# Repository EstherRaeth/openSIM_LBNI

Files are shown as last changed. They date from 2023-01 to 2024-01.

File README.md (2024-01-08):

logo_openSIM_2_web

## open-source structured illumination add-on for fluorescence microscopes

The resolution of conventional optical microscopes is limited by light diffraction to about 200nm. Several superresolution techniques have been recently developed to overcome this limit. Among them, **SIM (structured illumination microscopy)** is one of the most suited for biological imaging.

The **open source hardware project openSIM** is an **add-on** designed at the *Laboratory for Bio- and Nano- Instrumentation (LBNI, EPFL)* (https://www.epfl.ch/labs/lbni/) to **upgrade conventional fluorescence microscopes for superresolution imaging**. The openSIM is an open-source hardware project which has been designed specifically so that it can be built easily by other researchers using the documentation. Our goal is to reach labs worldwide and build a vibrant **open-hardware community**.

complete_system_plus_interfaceBox

**Here you can find a schematic of the general structure of the openSIM documentation**
overview_documentation

A detailed documentation with all the information to build and use the openSIM is provided on our openSIM webpage: 
**https://opensim.notion.site/**

All the files that need to be downloaded in order to assemble and operate the openSIM can be found in this repository. 
More information about the structure of this repository can be found in the README file in the download folder.

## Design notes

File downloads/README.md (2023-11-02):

## Navigating through the openSIM repository:

Below you can find the folder structure and the file content. 
Each folder contains README files with further information about the corresponding file. 

**CAD**
- 3D printing
- laser cutting
- machining
- Solidwork files

**electronics**
- PCB design

**software**
- image acquisition
- image processing

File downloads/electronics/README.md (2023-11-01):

**Electronics folder structure**

electronics_folderStructure

**Electronics folder content**

The files in the folder 'CAMOutputs' are required when ordering the PCB. 

(GerberFiles: Gerber files are a standard file format used in the manufacturing of printed circuit boards (PCBs). These files contain the information necessary to guide the PCB fabrication process and ensure that the PCB is manufactured to the design specifications. Gerber files typically include data on the various layers of the PCB, such as the copper traces, solder mask, silkscreen, drill holes, and other relevant features. PCB design software generates these files, and they are then provided to a PCB manufacturer for the production of the actual circuit board.)

In the folder 'additional information' information on the PCB population can be found. The folder contains also a subfolder 'EAGLE_files' containing the PCB design files (.brd, .sch) in case a user seeks more information or wants to modify the board. These files have to be opened with the Eagle (electronic design software). A free version of Eagle can be downloaded here: http://eagle.autodesk.com/eagle/software-versions/7

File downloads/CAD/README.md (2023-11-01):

**3D printing:**
Here you can find the parts that need to be 3D printed for the openSIM add-on and interface box in STL format.
This file format is commonly used for 3D printing and is compatible with standard commercial 3D printers. 

**laser_cutting:**
Here you can find the parts that need to be laser cut for the openSIM add-on enclosure in DXF format 

**machining:**
Here you can find a drawing indicating the position of the holes that need to be drilled into the heat sink (LED cooling). 

**solidwork files:**
Here you find all parts and assemblies (SLDASM format) of the openSIM add-on and interface box. 
These files are not necessary for the assembly or usage of openSIM, but can be used for further modifications.

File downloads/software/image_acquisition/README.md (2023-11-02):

We currently offer three software versions to cater to various user requirements (see openSIM website section 'Additional information'-'openSIM software' for more information): 

**Full openSIM LabView Project Versions:** For users seeking to modify or customize the software, we provide two full LabView projects. The first version, "openSIM_software_withCameraControl," integrates complete camera control, including image acquisition and data handling, specifically designed for Andor Zyla and Andor iXon camera models, using the Andor SDK (software development kit) for LabView. 
We don't provide this software version on GitHub as it contains proprietary VIs from the Andor SDK3. However, if the user already has the Andor SDK3 then we can provide this software version on request. The second version maintains the same structure but omits camera-model-specific components, making it modular and adaptable for other camera models. 
To address the reviewer’s comment, we developed an additional software version based on which we built an application that we now provide on the openSIM repository. 

**openSIM Application (exe):** To overcome the need for any chargeable licenses and to offer a more open-source software option, we created an openSIM software version which allowed us to build an application from it. This software version is designed for user who primarily want to use the software without any need for modification. Running the software version doesn't require any paid software licenses and is not tied to a specific camera model.

overview_software_versions

If you encounter problems with the installation or running the software please check the troubleshooting guide (chapter 8) in the respective user manual.

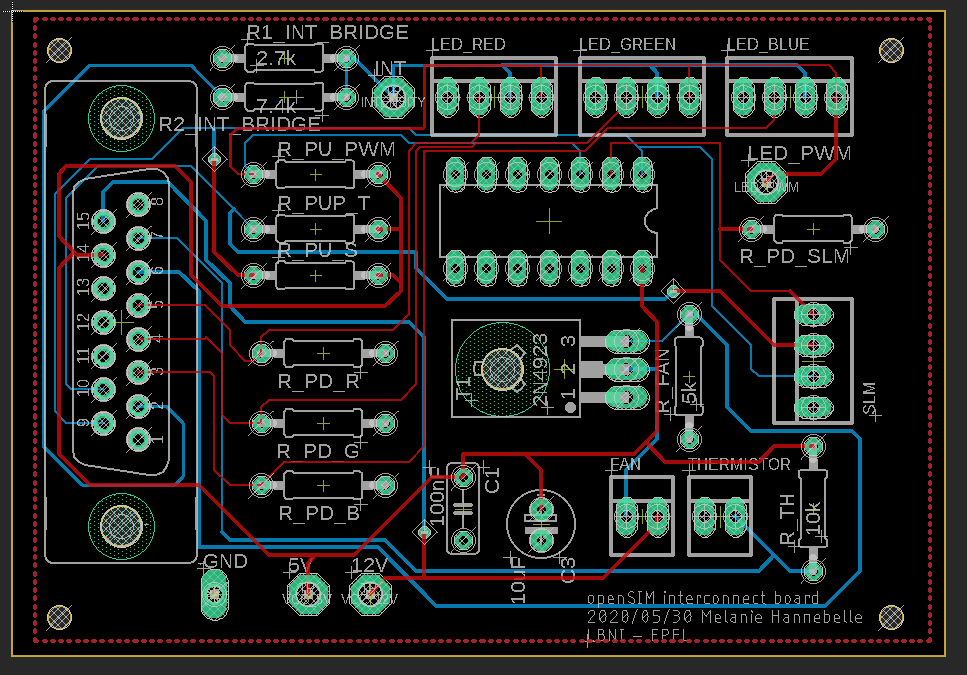
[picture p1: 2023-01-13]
downloads/electronics/additional_information/openSIM_interconnectBoard_PCB_layout.PNG

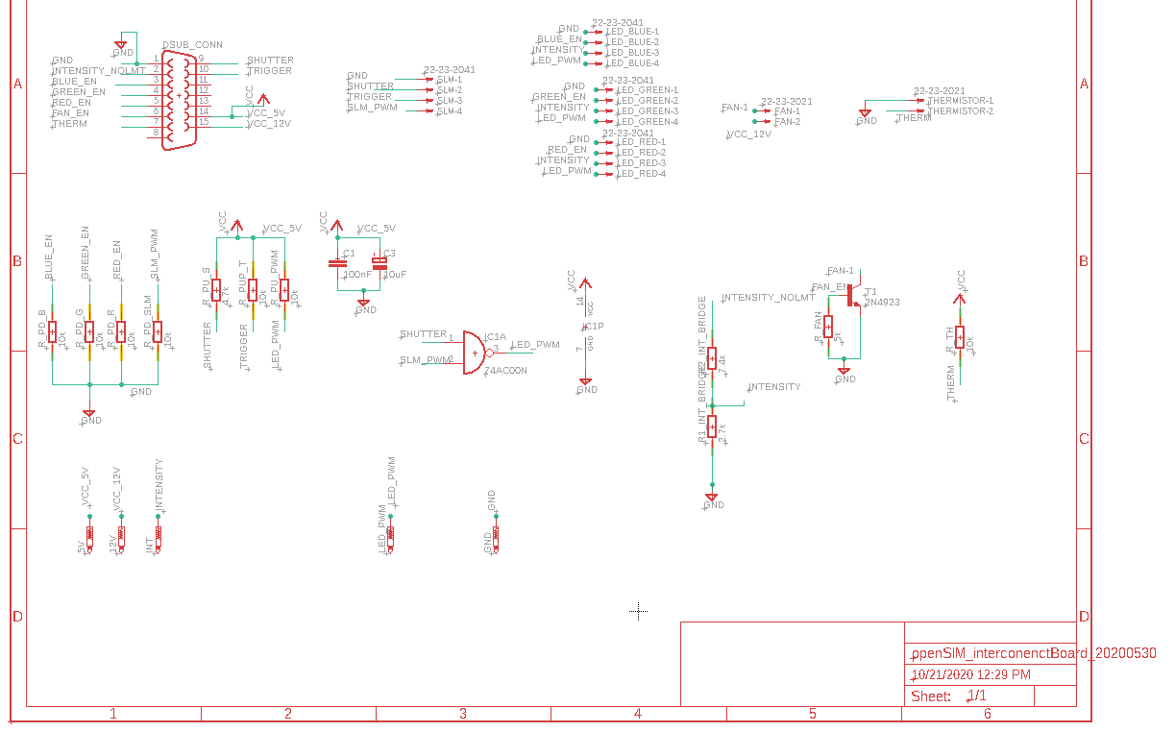
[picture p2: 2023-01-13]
downloads/electronics/additional_information/openSIM_interconnectBoard_PCB_schematic.PNG

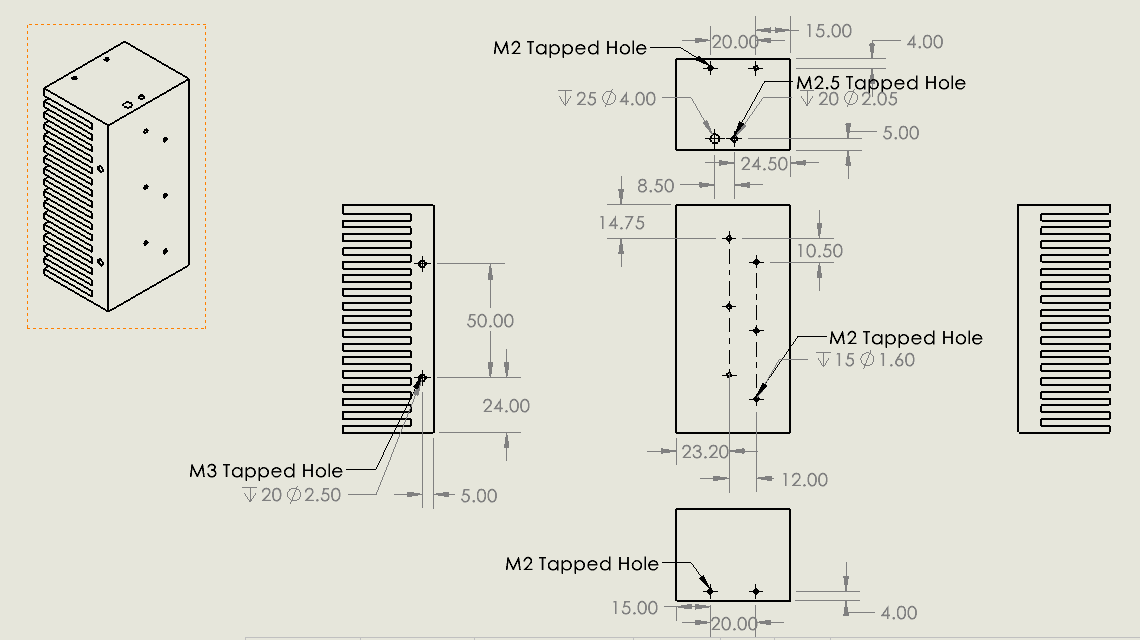
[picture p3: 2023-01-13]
downloads/CAD/machining/drawing_heatSink.png

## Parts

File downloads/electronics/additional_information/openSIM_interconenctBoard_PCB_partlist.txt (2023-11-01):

Partlist

Exported from openSIM_interconenctBoard_20200530.brd at 5/30/2020 7:35 PM

EAGLE Version 9.5.2 Copyright (c) 1988-2019 Autodesk, Inc.

Assembly variant: 

Part       Value          Package      Library       Position (mil)        Orientation

5V         PTR1PAD1-20    P1-20        testpad       (225 0)               R0
12V        PTR1PAD1-20    P1-20        testpad       (425 0)               R0
C1         100nF          C050-025X075 rcl           (725 275)             R270
C3         10uF           E2,5-6E      rcl           (975 225)             R270
DSUB_CONN                 F15V         con-subd      (-375 875)            R270
FAN        22-23-2021     22-23-2021   con-molex     (1300 250)            R0
GND        PTR1PAD1-13Y   P1-13Y       testpad       (25 0)                R0
IC1        74AC00N        DIL14        74xx-eu       (1000 1200)           R180
INT        PTR1PAD1-20    P1-20        testpad       (475 1600)            R0
LED_BLUE   22-23-2041     22-23-2041   con-molex     (1775 1600)           R0
LED_GREEN  22-23-2041     22-23-2041   con-molex     (1300 1600)           R0
LED_PWM    PTR1PAD1-20    P1-20        testpad       (1700 1325)           R0
LED_RED    22-23-2041     22-23-2041   con-molex     (825 1600)            R0
R_FAN      5k             0207/10      eagle-ltspice (1450 700)            R90
R_PD_B     50k            0207/10      eagle-ltspice (275 350)             R180
R_PD_G     50k            0207/10      eagle-ltspice (275 550)             R180
R_PD_R     50k            0207/10      eagle-ltspice (275 775)             R180
R_PD_SLM   5k             0207/10      eagle-ltspice (1850 1175)           R180
R_PUP_T    10k            0207/10      eagle-ltspice (250 1175)            R0
R_PU_PWM   10k            0207/10      eagle-ltspice (250 1350)            R0
R_PU_S     10k            0207/10      eagle-ltspice (250 1025)            R0
R_TH       5k             0207/10      eagle-ltspice (1850 275)            R90
SLM        22-23-2041     22-23-2041   con-molex     (1850 750)            R90
T1         2N4923         TO126        transistor    (1050 725)            R90
THERMISTOR 22-23-2021     22-23-2021   con-molex     (1550 250)            R0

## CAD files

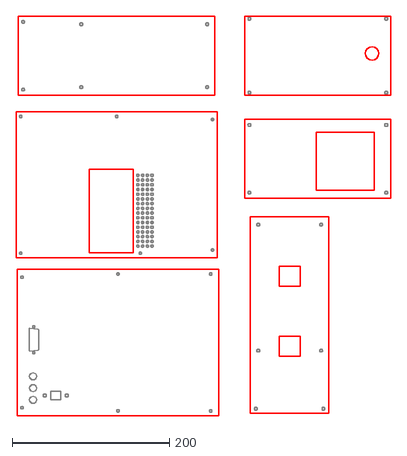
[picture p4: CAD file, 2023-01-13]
downloads/CAD/laser_cutting/assembly_PMMA_lasercut.dxf
476.8 x 507.7

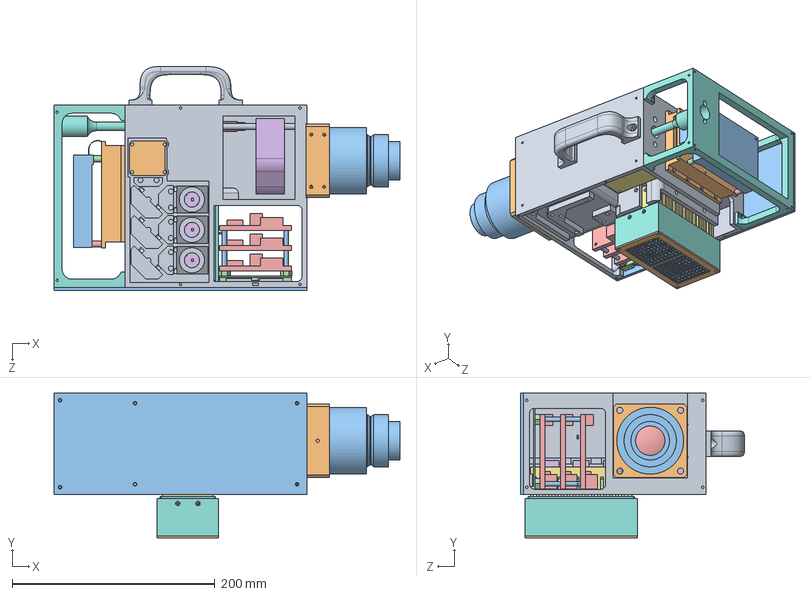
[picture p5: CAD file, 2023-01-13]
downloads/CAD/solidwork_files/openSIM_addOn_assembly/assembly_addOn_openSIM_V2.0.SLDASM
341.7 x 143.0 x 221.0 mm
optics_bloc_openSIM_V2.0
LCP11_M-thorlabs_openSIM_V2.0
SM2Y1-IllPortConnector_thorlabs_openSIM_V2.0
polarizing_beam_splitter_openSIM_V2.0
TTL200-A-tubelens_thorlabs_openSIM_V2.0
TubeLens_Holder_openSIM_V2.0
SSTMH8B_openSIM_V2.0
LMU_N6_openSIM_V2.0 x 2
ssfj6-100_openSIM_V2.0 x 2
SLM_holder_openSIM_V2.0
SLM_Model_Folded_openSIM_V2.0
SP-J3-8_20200728_openSIM_V2.0 x 2
SP-J3-10_20200728_openSIM_V2.0 x 2
PT54_20200728_openSIM_V2.0 x 3
heat_sink_openSIM_V2.0
fan_holder_openSIM_V2.0
fan_openSIM_V2.0
fan_protection_openSIM_V2.0
LED_boards__holder_openSIM_V2.0
LED_driver_board_openSIM_V2.0 x 3
LED_board_spacer_openSIM_V2.0 x 8
LBNR2_openSIM_V2.0 x 4
board_interface_openSIM_V2.0
structure_frame_openSIM_V2.0
handle_openSIM_V2.0
PBS_cover_openSIM_V2.0
panel_bottom_openSIM_V2.0
HANS10_60_3_openSIM_V2.0
HANS10_60_5_openSIM_V2.0

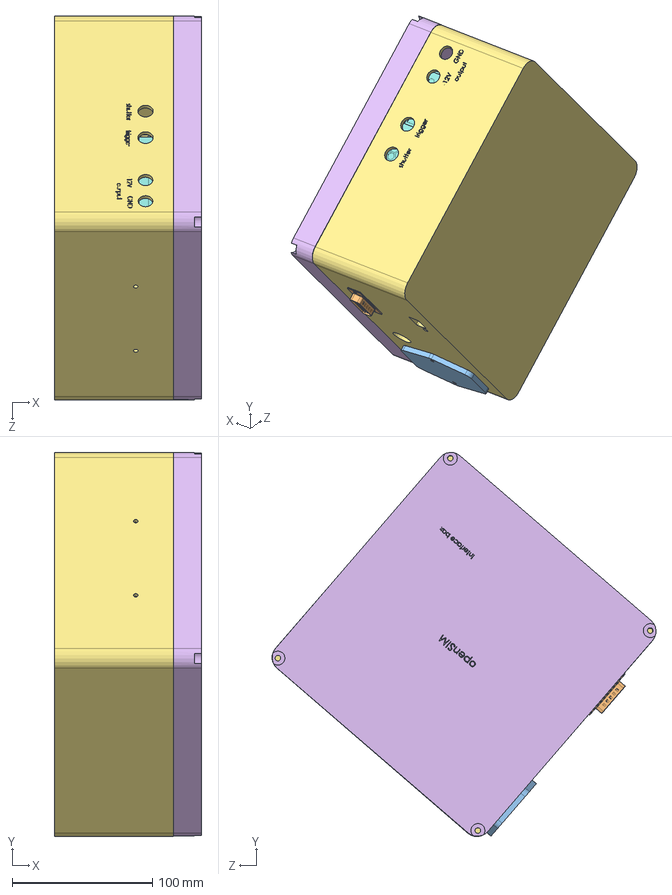
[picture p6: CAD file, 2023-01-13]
downloads/CAD/solidwork_files/openSIM_interfaceBox_assembly/Assem_openSIM_interfaceBox_2powerSupplies_openSIM_V2.0.SLDASM
105.0 x 274.0 x 274.0 mm
clamp_DAQ_openSIM_V2.0 x 2
D SUB 15P male_openSIM_V2.0
delta_06ab2d_openSIM_V2.0
interfaceBox_holder_powerSupply_openSIM_V2.0
NI_USB_6001_daq_openSIM_V2.0
openSIM_interface_box_cover_openSIM_V2.0
openSIM_interface_box_lowerPart
powerSupply1_openSIM_V2.0
powerSupply2_openSIM_V2.0

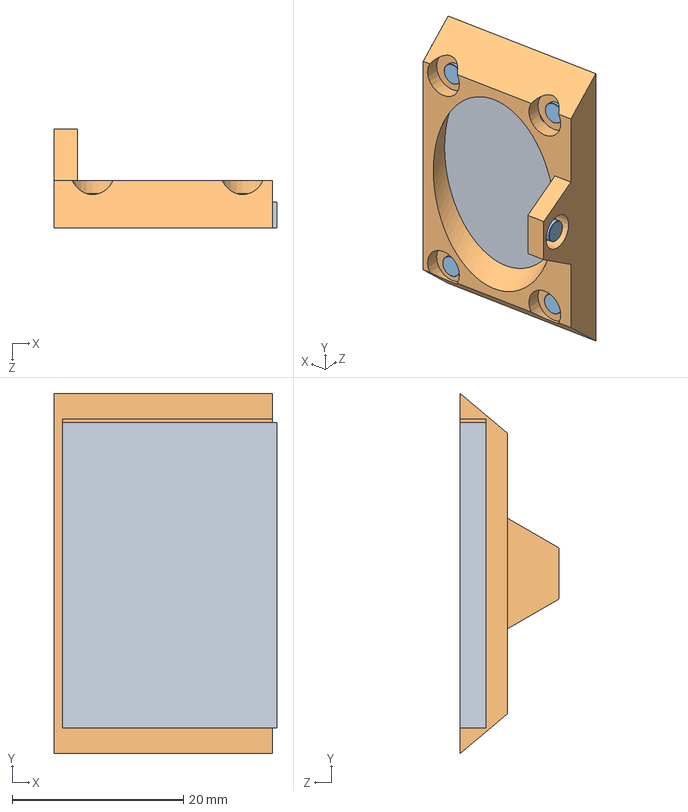
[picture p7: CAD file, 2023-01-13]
downloads/CAD/solidwork_files/openSIM_addOn_assembly/assembly_holder_mirror_20200806.SLDASM
26.0 x 42.0 x 11.5 mm
mirror_20200728
holder_mirror_20200806
HXN3_1_20200728 x 5

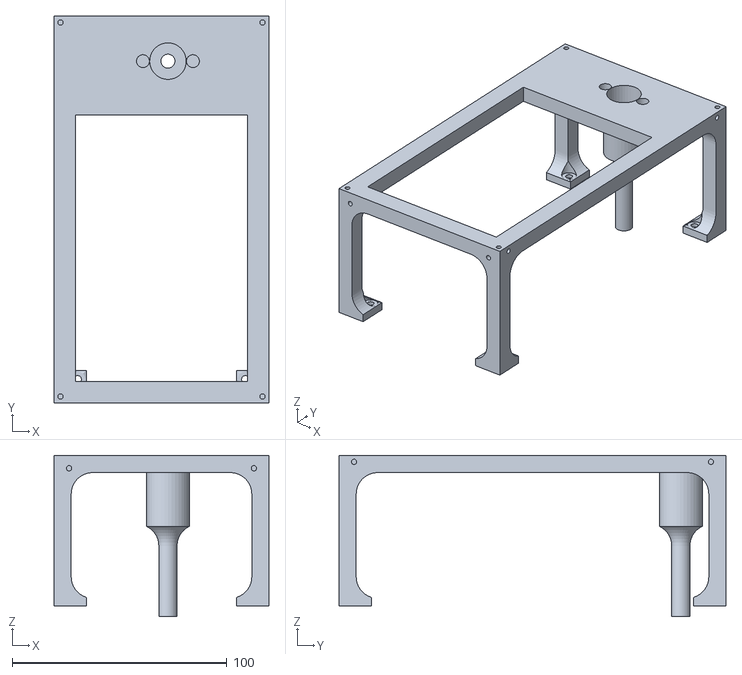
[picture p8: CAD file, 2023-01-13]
downloads/CAD/3D_printing/add_on/structure_frame_openSIM_V2.0.STL
100.0 x 180.0 x 75.0

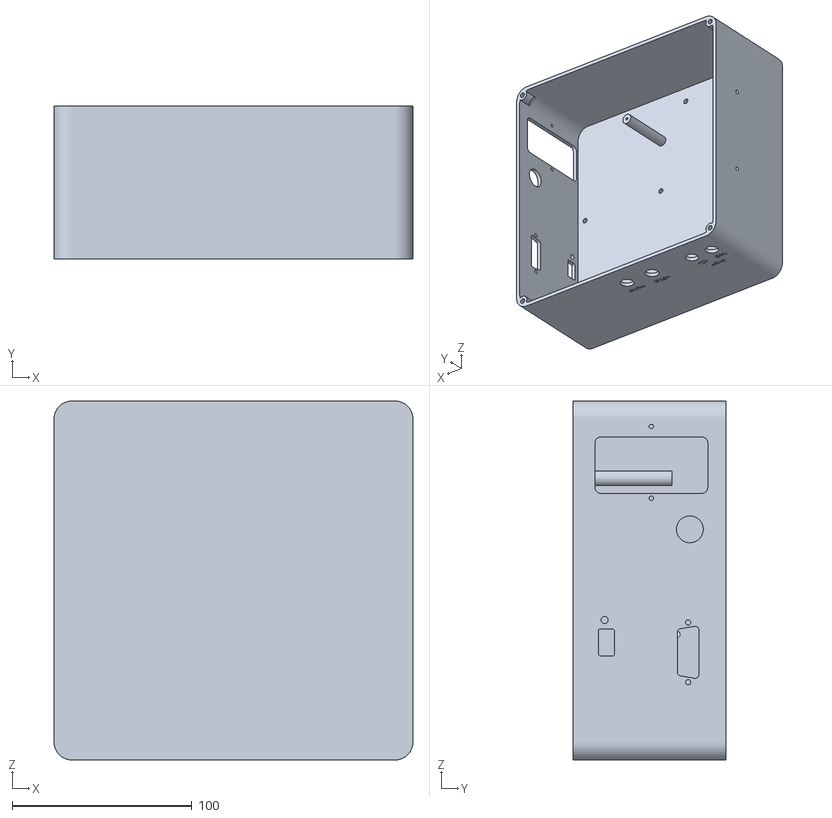
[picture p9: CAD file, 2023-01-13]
downloads/CAD/3D_printing/interface_box/openSIM_interface_box_lowerPart.STL
200.0 x 85.0 x 200.0

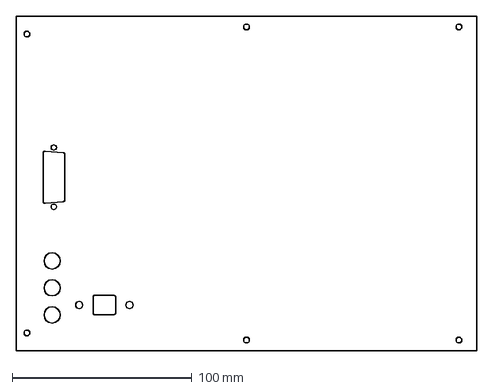
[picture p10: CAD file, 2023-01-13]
downloads/CAD/laser_cutting/panel_front_openSIM_V2.0.DXF
256.0 x 186.0 mm

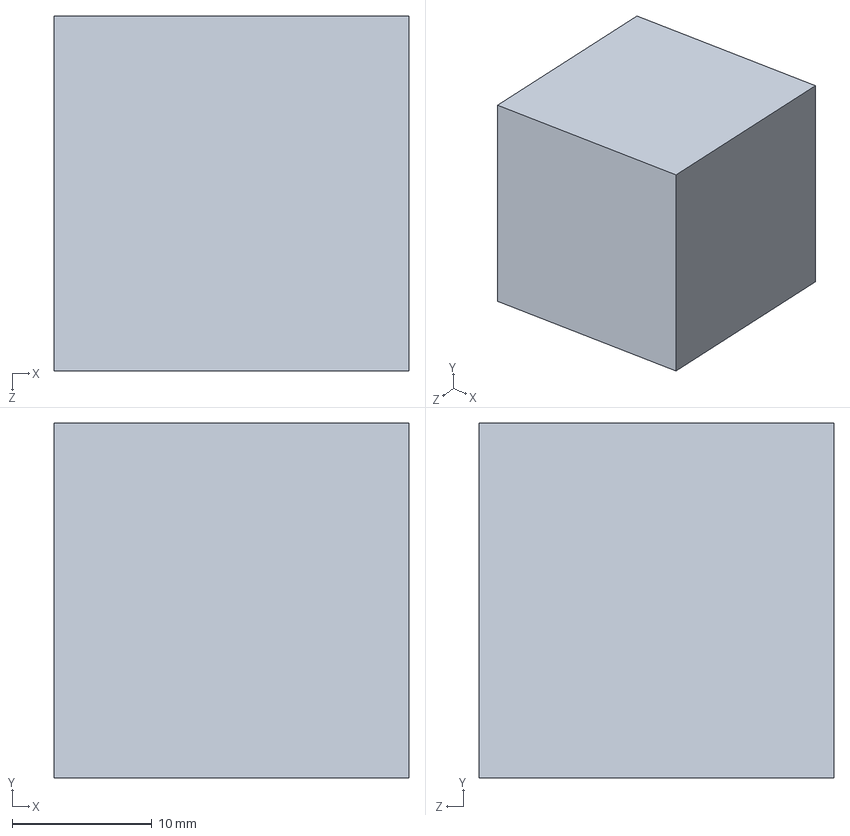
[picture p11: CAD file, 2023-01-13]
downloads/CAD/solidwork_files/openSIM_addOn_assembly/polarizing_beam_splitter_openSIM_V2.0.SLDPRT
25.4 x 25.4 x 25.4 mm

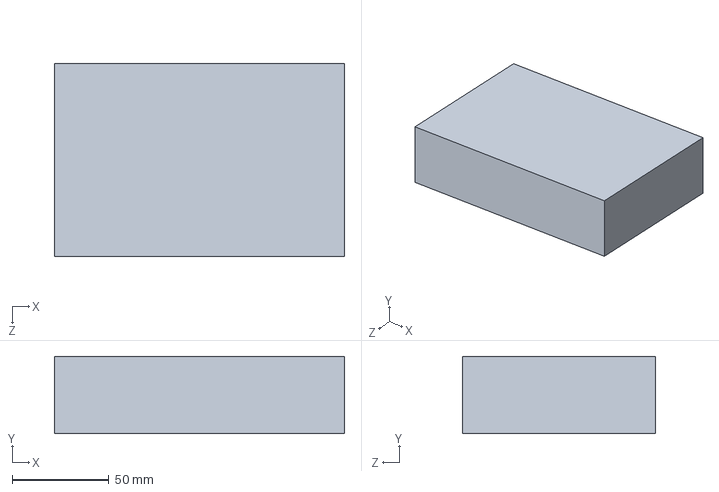
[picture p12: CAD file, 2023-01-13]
downloads/CAD/solidwork_files/openSIM_interfaceBox_assembly/powerSupply2_openSIM_V2.0.SLDPRT
150.0 x 40.0 x 100.0 mm

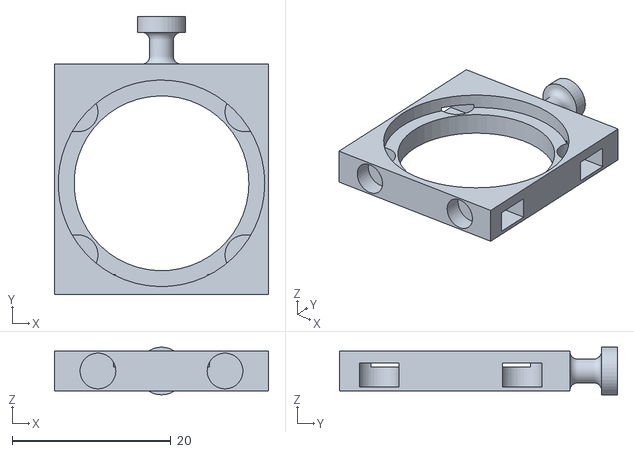
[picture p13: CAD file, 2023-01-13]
downloads/CAD/3D_printing/add_on/collimator_lens_holder_openSIM_V2.0.STL
27.0 x 35.0 x 6.00

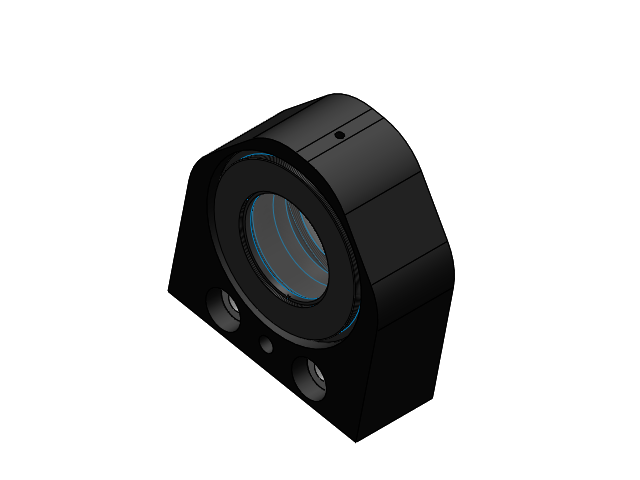
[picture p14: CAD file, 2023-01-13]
downloads/CAD/solidwork_files/openSIM_addOn_assembly/assembly_tube_lens_openSIM_V2.0.SLDASM
TTL200-A-tubelens_thorlabs_openSIM_V2.0
TubeLens_Holder_openSIM_V2.0
SSTMH8B_openSIM_V2.0
LMU_N6_openSIM_V2.0 x 2

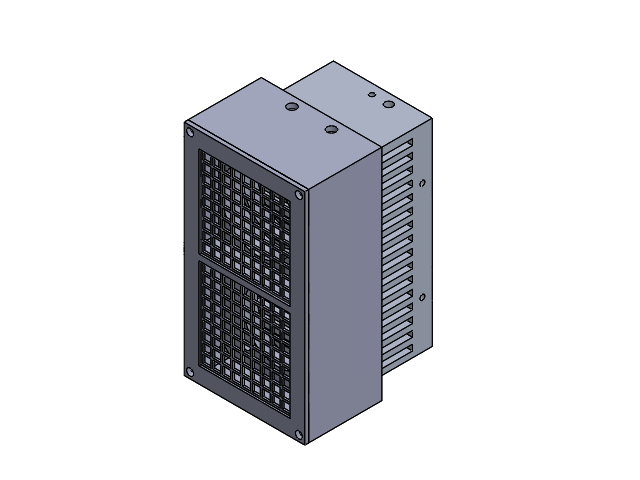
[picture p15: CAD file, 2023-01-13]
downloads/CAD/solidwork_files/openSIM_addOn_assembly/assembly_LEDs_openSIM_V2.0.SLDASM
PT54_20200728_openSIM_V2.0 x 3
heat_sink_openSIM_V2.0
fan_holder_openSIM_V2.0
fan_openSIM_V2.0
fan_protection_openSIM_V2.0

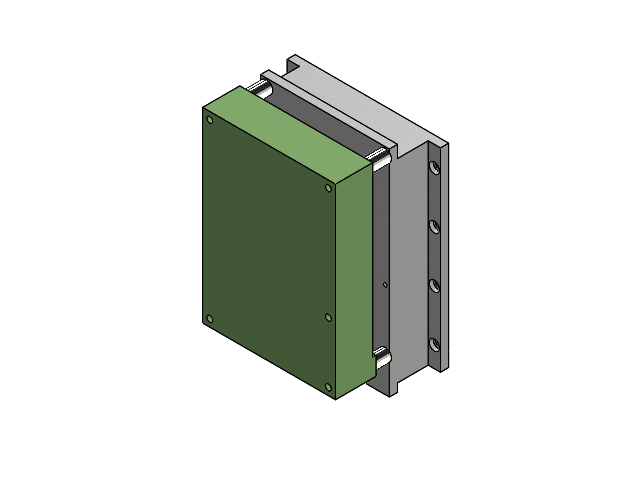
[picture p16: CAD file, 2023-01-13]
downloads/CAD/solidwork_files/openSIM_addOn_assembly/assembly_slm_openSIM_V2.0.SLDASM
SLM_holder_openSIM_V2.0
SLM_Model_Folded_openSIM_V2.0
SP-J3-8_20200728_openSIM_V2.0 x 2
SP-J3-10_20200728_openSIM_V2.0 x 2

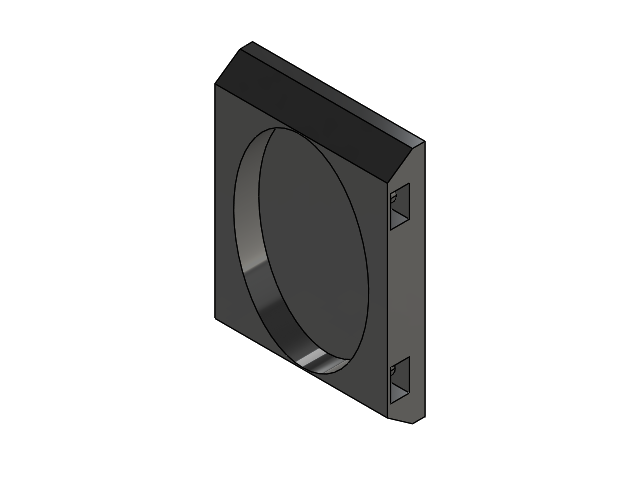
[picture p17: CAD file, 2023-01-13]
downloads/CAD/solidwork_files/openSIM_addOn_assembly/assembly_holder_colorCombiner_dichroic_openSIM_V2.0.SLDASM
HXN3_1_openSIM_V2.0 x 4
holder_colorCombiner_dichroic_openSIM_V2.0
dichroicMirror_openSIM_V2.0

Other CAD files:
downloads/CAD/solidwork_files/openSIM_addOn_assembly/assembly_collimator_openSIM_V2.0.SLDASM
downloads/CAD/solidwork_files/openSIM_addOn_assembly/assembly_LEDs_boards_openSIM_V2.0.SLDASM
downloads/CAD/solidwork_files/openSIM_addOn_assembly/assembly_polarizer_openSIM_V2.0.SLDASM
downloads/CAD/solidwork_files/openSIM_addOn_assembly/assembly_holder_colorCombiner_mirror_openSIM_V2.0.SLDASM
downloads/CAD/3D_printing/add_on/LED_boards__holder_openSIM_V2.0.STL
downloads/CAD/3D_printing/add_on/SLM_holder_openSIM_V2.0.STL
downloads/CAD/3D_printing/add_on/TubeLens_Holder_openSIM_V2.0.STL
downloads/CAD/3D_printing/add_on/cap_screwdriver_openSIM_V2.0.STL
downloads/CAD/3D_printing/add_on/fan_holder_openSIM_V2.0.STL
downloads/CAD/3D_printing/add_on/fan_protection_openSIM_V2.0.STL
downloads/CAD/3D_printing/add_on/handle_openSIM_V2.0.STL
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

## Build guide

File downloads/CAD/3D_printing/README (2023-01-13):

Here you can find the parts which need to be 3D printed in STL format  (file format commonly used for 3D printing)

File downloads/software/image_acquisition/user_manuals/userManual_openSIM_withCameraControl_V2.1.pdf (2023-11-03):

# User manual openSIM software

# software version: with integrated camera control

## Contents

## 1. Structure openSIM user manual:

- The main part of the user interface describes operating the openSIM software in normal operating mode which includes all the controls and indicators necessary for SIM image acquisition.
- For testing and troubleshooting purposes the expert mode can be used (see appendix) during which additional status and log information are displayed.
- The user interface is categorized in controls (user can enter information) and indicators (information are displayed to user)
- Currently the control for two different cameras (Andor Zyla and Andor iXon) is implemented in the software. As camera setting are mostly specific for one camera type, the corresponding descriptions are marked in grey

## 2. Introduction to the openSIM software

The openSIM software is written with LabView. It controls the openSIM device itself and interfaces additional components such as the camera and piezo focus positioner if available. It includes a user interface to enter the necessary parameters and to display currently executed commands and error messages. The part of the software operating the openSIM device controls the LEDs, provides the pattern sequence for the spatial light modulator (SLM), and actuates the fan. The projected pattern sequences can be selected either manually from a list of pattern sequences or automatically based on parameter inputs from the user. The software handles the image mode selection, saving and formatting of the acquired data and the corresponding metadata. In addition, the software controls the camera for the image acquisition. If a device necessary for z-stacking, such as a piezo focus positioner or a motorized focus controller, is available, the software can be used to perform z-stacking. The z-stacking function automatically changes the focus of the objective by providing an analog output to the focus adjusting device.

The software is written in a modular structure to enable a customization and adaption to different peripheral components such as different camera models or focus adjustment. The current version of the software includes an integration for an Andor Zyla sCMOS, an Andor iXon EMCCD camera (information specifically relevant for these two camera types are marked in grey in the following text) and Piezosystem Jena Mipos 100 piezo focus positioner. For controlling the Andor cameras a software development kit provided by Andor (SDK 3 for LabView) is used. The SDK contains a dynamic library from which we used functions to enable and execute the configuration and data acquisition process of the camera.

See the documentation of openSIM software (provided within the distributed openSIM documentation folder) for more detailed information on the LabView code.

## 3. Installation

### 1. Microsoft Visual Studio

Install Microsoft Visual Studio Express 2013. You may encounter compatibility issues if you attempt to run the openSIM software with a different version of Visual Studio. A key is not required for the installation of the Express version.
Download: https://visualstudio.microsoft.com/vs/older-downloads/

This will download an ISO file. To access to setup.exe file in order to install the software you can either mount (right-click on ISO file → mount command) the file (opens a virtual drive that is visible in the file explorer) or extract the files (right-click on ISO file → extract)

### 2. LabView

Install LabView 2018 SP1 including the vision development module and DAQmx module. The openSIM software was created with LabView 2018 SP1.
Download: https://www.ni.com/en-us/support/downloads/software-products/download.labview.html#329059 (https://www.ni.com/en-us/support/downloads/software-products/download.labview.html#329059)
➔ Vision development module: https://www.ni.com/en-us/support/downloads/software-products/download.vision-development-module.html#329460 (https://www.ni.com/en-us/support/downloads/software-products/download.vision-development-module.html)
➔ DAQmx module: https://www.ni.com/en-us/support/downloads/drivers/download.ni-daqmx.html#333268 (https://www.ni.com/en-us/support/downloads/drivers/download.ni-daqmx.html#333268)

### 3. MetroCon

Run the MetroCon 3.3 application from the MetroCon folder provided in the openSIM repository in the image acquisition folder within the software folder
Check that MetroCon is installed in C:\Program Files…

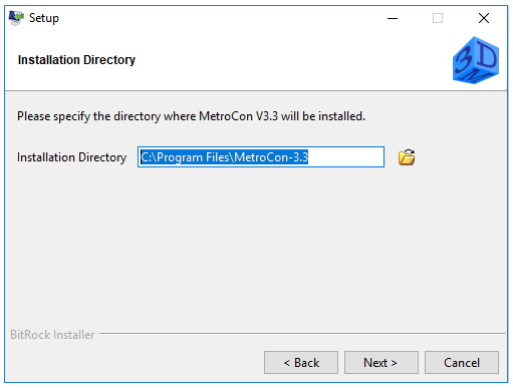
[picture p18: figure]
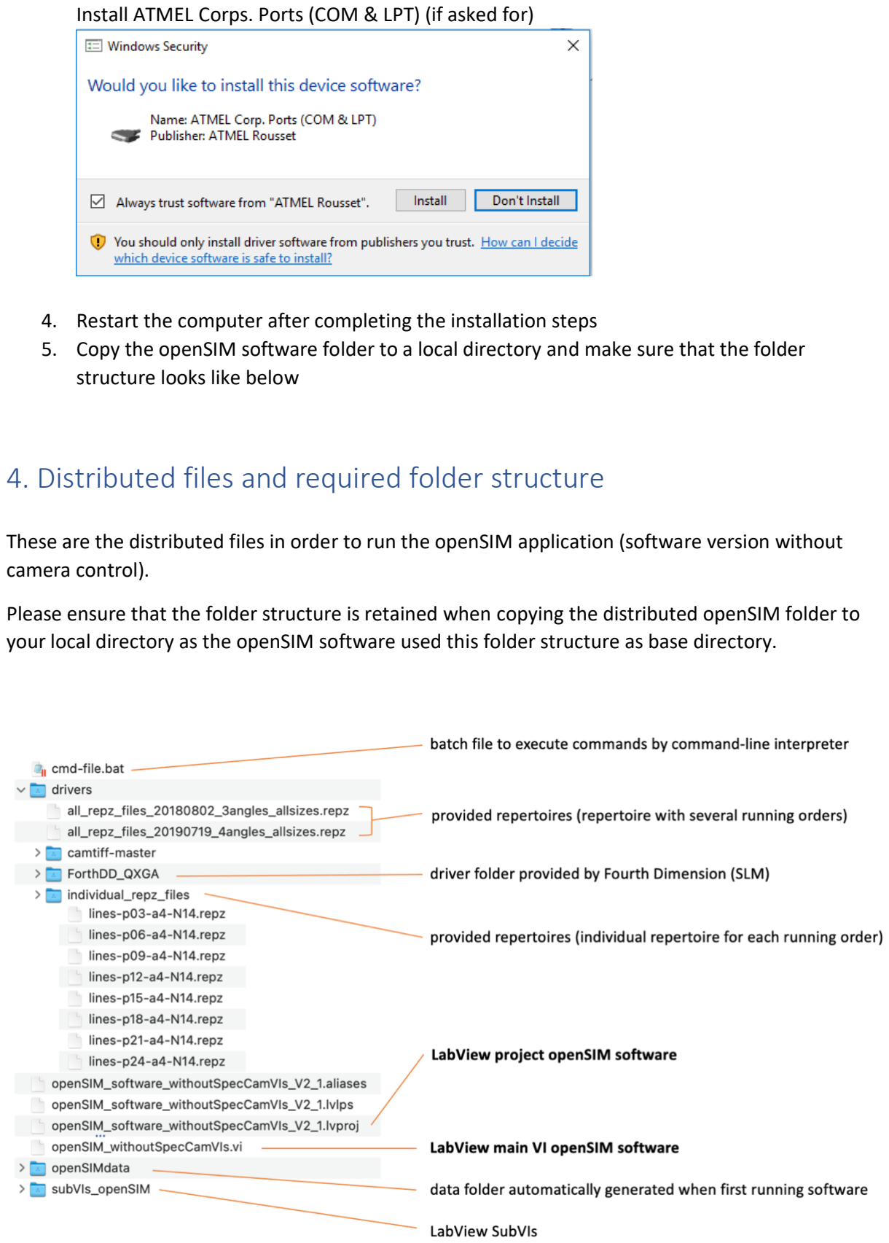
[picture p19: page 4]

Install ATMEL Corps. Ports (COM & LPT) (if asked for)

4. Restart the computer after completing the installation steps
5. Copy the openSIM software folder to a local directory and make sure that the folder structure looks like below

## 4. Distributed files and required folder structure

These are the distributed files in order to run the openSIM application (software version without camera control).

Please ensure that the folder structure is retained when copying the distributed openSIM folder to your local directory as the openSIM software used this folder structure as base directory.

## 5. Illumination patterns

For SIM image reconstruction, the sample needs to be illuminated with a set of patterns with different phases and angles. We generated different line illumination patterns (according to SIMToolbox – supplementary documentation and user’s guide) which are distributed with the openSIM software. For a better understanding we provide here some background information and explain the used terminology.

Pattern sequence:
- sequence of patterns projected by the SLM during the SIM image acquisition
- each pattern of the sequence has a different phase and angle → the number of patterns in the sequence defines the total number of images during one SIM image acquisition (one image is acquired per pattern and the total amount of images is saved as an image stack)
- pattern sequence is stored as repertoire (.repz file format), a zip file containing:
- images of the pattern (.bmp file format)
- timing schedule (.seq file format, supplied by Forth Dimension, defines the bright and dark phases of the SLM)
- running order (.rep file format, describes the order of the projected pattern images in the sequence and the and trigger mode)
- a pattern sequence can contain several running orders (rep file with description of several running orders)
- we provide the generated pattern sequences in two ways:
- repertoire with several running orders (repz files: all_patternSequences_3angles.repz; all_patternSequences_4angles.repz): repertoire to be uploaded to the SLM, the running orders define the different available individual sequences of pattern which can be projected by the SLM
- repertoire with one running order: when using the SIMToolbox for SIM image reconstruction, the software requires information about the pattern sequence projected during the SIM image acquisition, the software can automatically read in the pattern information when stored in a specifically formatted text file (.yaml file format)
→ to facilitate the automatic read in of the pattern description file, we provide a folder (individual_patternSequences) which contains an individual repertoire (repz files: lines-p03-a4-N14.repz, ….) for each running order (lines-p03-a4-N14,…) available in the provided repertoires descripted above (all_patternSequences_3angles.repz; all_patternSequences_4angles.repz), when acquiring a SIM image the individual repertoire corresponding to the used running order is saved together with the acquired data

Terminology for openSIM user interface and user manual:
→ for a better differentiation we use the term ‘repertoire’ for .repz files and the term ‘pattern sequence’ for the actually, by the running order defined and by the SLM projected, sequence of patterns during a single SIM image acquisition

## 6. Control of the openSIM software

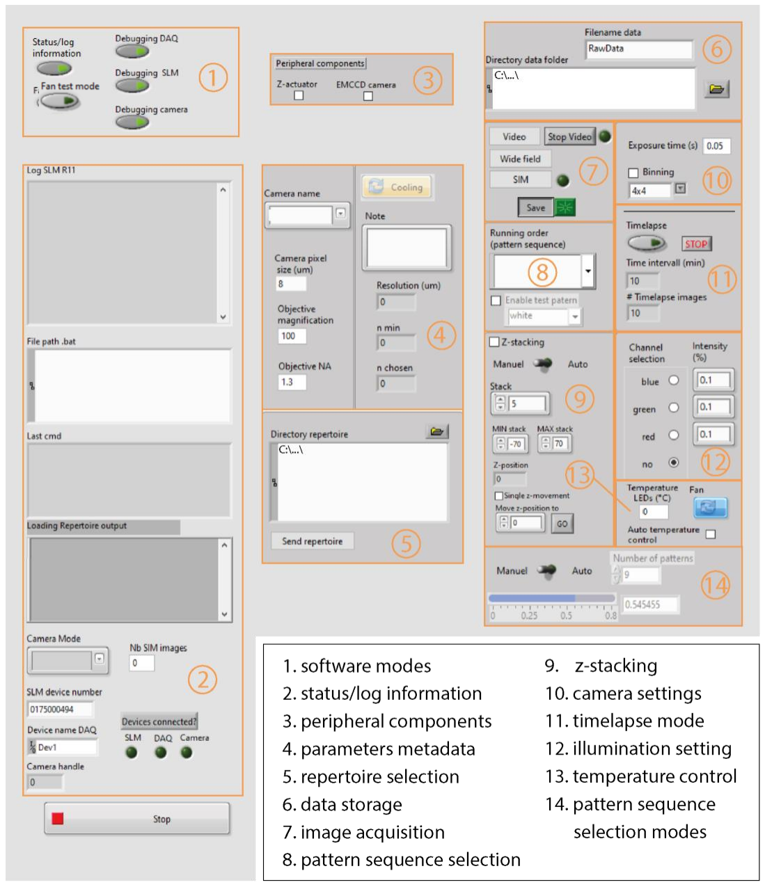
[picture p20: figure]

Overall structure of complete openSIM user interface

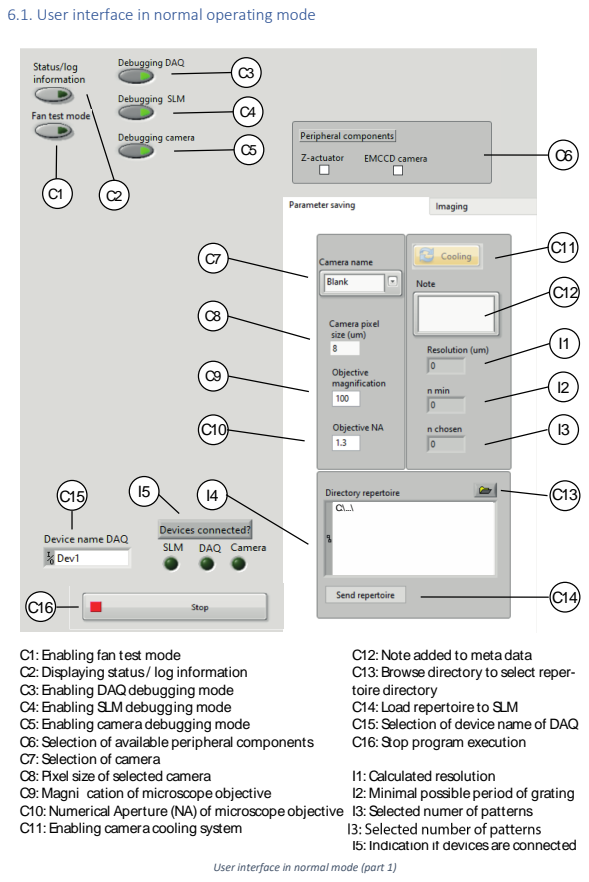
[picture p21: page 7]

6.1. User interface in normal operating mode

C1: Enabling fan test mode
C2: Displaying status / log information
C3: Enabling DAQ debugging mode
C4: Enabling SLM debugging mode
C5: Enabling camera debugging mode
C6: Selection of available peripheral components
C7: Selection of camera
C8: Pixel size of selected camera
C9: Magni cation of microscope objective
C10: Numerical Aperture (NA) of microscope objective
C11: Enabling camera cooling system

C12: Note added to meta data
C13: Browse directory to select reper-
toire directory
C14: Load repertoire to SLM
C15: Selection of device name of DAQ
C16: Stop program execution

I1: Calculated resolution
I2: Minimal possible period of grating
I3: Selected numer of patterns
I4: Directory repertoire
I5: Indication if devices are connected

User interface in normal mode (part 1)

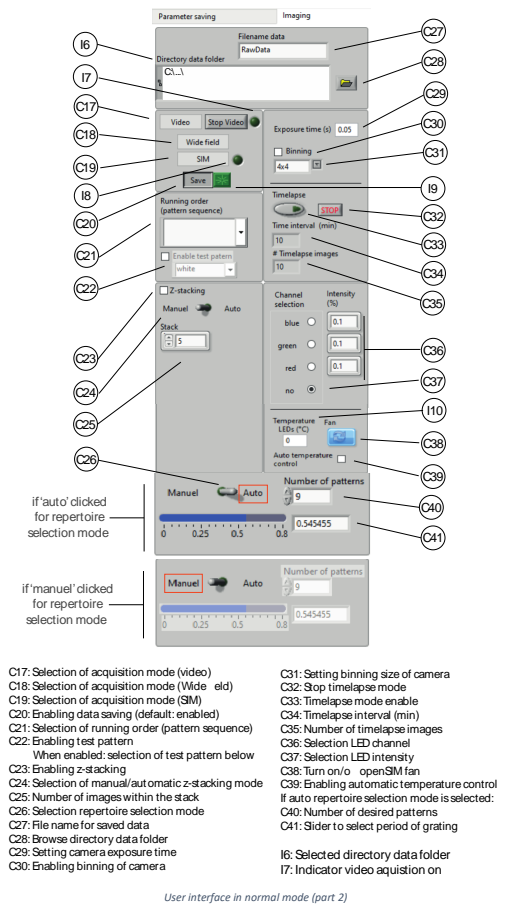
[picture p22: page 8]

C17: Selection of acquisition mode (video)
C18: Selection of acquisition mode (Wide eld)
C19: Selection of acquisition mode (SIM)
C20: Enabling data saving (default: enabled)
C21: Selection of running order (pattern sequence)
C22: Enabling test pattern
When enabled: selection of test pattern below
C23: Enabling z-stacking
C24: Selection of manual/automatic z-stacking mode
C25: Number of images within the stack
C26: Selection repertoire selection mode
C27: File name for saved data
C28: Browse directory data folder
C29: Setting camera exposure time
C30: Enabling binning of camera

C31: Setting binning size of camera
C32: Stop timelapse mode
C33: Timelapse mode enable
C34: Timelapse interval (min)
C35: Number of timelapse images
C36: Selection LED channel
C37: Selection LED intensity
C38: Turn on/o openSIM fan
C39: Enabling automatic temperature control
If auto repertoire selection mode is selected:
C40: Number of desired patterns
C41: Slider to select period of grating

I6: Selected directory data folder
I7: Indicator video aquistion on

User interface in normal mode (part 2)

### 6.2. Input parameters

→ Depending on certain selections/modes some of the indicators and controls are greyed out. These controls and indicators are clickable when the corresponding mode is selected.

INDICATORS:

I1: Calculated resolution in µm
→ based on wavelength of selected channel and NA of objective (C37, C10)

I2: Calculated minimal spatial period
→ only relevant for auto running order (pattern sequence) selection mode
→ based on calculated resolution (I1), camera pixel size (C8) and magnification of objective (C9)

I3: Selected spatial period
→ only relevant for auto running order (pattern sequence) selection mode

I4: Directory of SLM repertoire
→ path to chosen repertoire (.repz file)
→ default: path to the .repz file which is included in the distributed openSIM software folder

I5: Indicator showing if devices (SLM, DAQ, Camera) are connected

I6: Display showing the selected folder where the acquired data is saved in

I7: Indicator showing if video acquisition is currently running

I8: Indicator showing if SIM acquisition is currently running

I9: Indicator showing if saving of the acquired images is currently enabled
→ images are saved in directory selected with C28 and showed in I6

I10: Temperature measured by thermistor at illumination block holding the PT54 LEDs
→ temperature is used as input for the temperature control system
→ if the temperature is too high, the two fans at the aluminum heat sink extender are turned on

CONTROLS:

C1: Enabling/Disabling expert mode (normal mode is default)
→ expert mode includes additional indicators which support debugging (in the expert mode indicator I10-I17 are visible)
→ see appendix for more information about the expert mode

C2: Enabling/Disabling fan test mode
→ if test mode is enabled, only the fan is controlled

Debugging modes:
- In order to facilitate testing and debugging of the software and the individual devices (i.e. SLM, NI DAQ, camera) it can be useful to connect only some of the devices (e.g. only NI DAQ is connected and tested with the software, while the SLM and camera are not connected). However, in the normal (non-debugging) mode the openSIM software will return an error message and stops when devices are not connected (e.g. because of missing device handles when the device is not connected which are needed in the initialization step). In the debugging mode, the software can be used despite the corresponding device not being connected.
- Debugging mode can be used for only one device or several devices at the same time

C3: DAQ debugging mode
→ facilitates the testing of functions independent of the DAQ devise
→ if enabled, the software does not try to connect to the DAQ device, software can be used even if the NI DAQ is not connected

C4: SLM debugging mode
→ facilitates the testing of functions independent of the SLM devise
→ if enabled, the software does not try to connect to the SLM device, software can be used even if the SLM is not connected

C5: Camera debugging mode
→ facilitates the testing of functions independent of camera
→ if enabled, the software does not try to connect to the camera, software can be used even if the camera is not connected

C6: Selecting the available peripheral components
→ specific controls are visible/invisible depending on the availability of the corresponding peripheral component
→ Z-actuator: should be selected if an actuator for changing the z-position of the microscope such as a piezo focus positioner, stepper motor or automated microscope is available and implemented. If enabled, the controls C38-42 are visible
(see section 5 for more information how to implement a z-actuator and see appendix for more information about the user interface for automated z-positioning)
→ EMCCD camera: should be selected if a EMCCD camera, where the EM gain can be changed, is implemented and used. If enabled, the controls C43-C44 are visible
(see section 5 for more information how to implement a camera and see appendix for more information about the additional control for a EMCCD camera)

C7: Selection of camera from list of implemented camera interfaces
→ see appendix for information how to include an interface for a different camera
→ select Andor iXon for Andor iXon EMCCD camera
→ select Andor Zyla for Andor Zyla sCMOS camera

C8: Pixel size of selected camera in µm
→ see the specification sheet of your camera for information about the pixel size → sCMOS camera Andor Zyla 4.2: pixel size is 6.5µm
→ EMCCD camera Andor iXon: pixel size is 13µm

C9: Magnification of microscope objective

C10: Numerical aperture (NA) of microscope objective

C11: Enabling/Disabling cooler (relevant if the camera includes a cooling system)
→ see the specification sheet of your camera to see whether it includes a cooling system
→ see appendix for information about the control of a camera cooling system when including a different camera
→ EMCCD camera Andor iXon has a deep vacuum cooling
→ sCMOS camera Andor Zyla 4.2 has no cooling option

C12: saved note in SIM mode
→ when acquiring SIM images, a text file containing meta data such as the imaging parameter settings are saved
→ the inserted note is added to the saved text file in SIM mode

C13: Browse directory to select file path to the repertoires (.repz file)
→ selected repertoire which is loaded to the SLM
→ default: path to the file ‘all_patternSequences_4angles.repz’

C14: Loading repertoires to SLM (selected with C13 and displayed at I4)

→ repertoires (.repz file) have to be loaded only once to the SLM

C15: Device name of connected data acquisition (DAQ) device
→ device name is shown when USB cable of DAQ device is connected to the PC
(see operation instructions for more information)

C16: Stop button to stop the program execution

C17: Selection of acquisition mode → video: mainly for test purpose, continuous acquisition of widefield images without a saving option

C18: Selection of acquisition mode → widefield: acquisition of widefield images, default: one image is acquired when bottom is clicked, if z-stacking is
enabled: number of total images equals number of stacks (C25) C19: Selection of acquisition mode → SIM: acquisition of SIM image stack, number of total images depends on the number of patterns in selected pattern sequence and number of stacks (C25) if z-stacking is enabled

C20: Enabling/Disabling data saving
→ acquired data is saved as .tiff file
→ in the SIM mode, the metadata (number of SIM datasets, number of pixels (x,y), camera pixel size, exposure time, EM gain, microscope magnification, channel selection) is saved as .txt file located at the file path specified by saving path (I6), saving is enabled by default

C21: Selection of running order (pattern sequence) selection mode
→ manual running order selection mode: the user manually selects the running order (pattern sequence from the list of running orders available for uploaded repertoire in the dropdown menu → auto running order selection mode: the control serves as a display which shows the automatically chosen running order (see C21 for more information about the running order selection mode)

C22: Enabling/Disabling test pattern
→ default: test pattern disabled (greyed out when test pattern is disabled)
→ if test pattern is enabled, different projected test patterns can be selected
→ possible test pattern: black, white, vertical bars

C23: Enabling/Disabling z-stacking
→ widefield mode: the z-position of the microscope objective is changed in steps and one image is acquired per step, the number of images in the stack is defined by C25
→ SIM mode: the z-position of the microscope objective is changed in steps and for every step several SIM images are acquired, the number of images in the stack in defined by C25 and C36 (default: z-stacking disabled)

C24: Selecting manual or automatic z-stacking mode
→ manual mode: the user has to select the starting z-position of the microscope objective and has to manually change the z-position by using the focus adjustment knob of the microscope before acquiring the next image of the z-stack
→ automatic mode: the focus is automatically changed by an actuator according to the z-stacking input parameter during the image acquisitions
(see appendix for more information about the automatic stacking mode)

C25: Number of images in the stack

C26: Running order (pattern sequence) selection mode
→ default: manual mode (if manual mode selected C36, C37 are greyed out)
→ manual mode: the user has to select the desired running order (pattern sequence) from the list of running orders (C21) available for the uploaded repertoire (I4)
→ auto mode: the running order (pattern sequence) is automatically selected based on the selected period (I3) and the desired number of projected patterns in the sequence(C36)

C27: File/folder name of saved data
→ The file name is automatically appended with an XXX-digit number for consecutive images → widefield acquisition mode: inserted name defines the name of the image (.tiff file) which is saved at the location defined by C24 and showed in I6
→ SIM acquisition mode: inserted name defines the name of an automatically created folder where the image (.tiff file), the metadata (.txt file) and the projected pattern (.repz file) are saved in

C28: Browse directory to select path to folder where the data is saved in (default: path to folder ‘openSIMdata’ the directory containing the application)

C29: Exposure time of camera in seconds

C30: Enabling/Disabling binning
→ only implemented for Andor Zyla sCMOS camera
→ sCMOS camera Andor Zyla: if binning is disabled the area of interest (AOI) is set back to 1048 pixel, if binning is enabled the pixel binning is set to the binning size defined by C31

C31: Binning size of camera
→ possible options are 2x2, 3x3, 4x4, 8x8

C32: Stop timelapse mode
→ stops timelapse imaging before last timelapse image is acquired
→ normally timelapse mode stops after acquisition of last timelapse image

C32: Enable timelapse mode
→ only for SIM image acquisition mode
→ if enabled, SIM image stacks are acquired in an interval defined by C34
→ first image is acquired when SIM image acquisition mode is selected (C19)
→ number of acquired SIM images is defined by C35
→ each SIM image stack is saved individual and not as a time stack since individual SIM image stacks are required for image reconstruction

C34: Time interval
→ defines the time period in min between two subsequent SIM image acquisitions

C35: # Timelapse images
→ defines the number of total timelapse images are acquired
→ total timelapse session: time interval * (# Timelapse images – 1)

C36: LED excitation intensity in %

C37: Selection of channel
→ indicates color of excitation light (blue, green, red LED)
(default setting is no LED selected)

C38: Manually turning the two fans which are mounted to the SIM device on/off → are also controlled by an automatic temperature control
→ fans are at the aluminum heat sink extender

C39: Enabling automatic temperature control

C40: Number of desired patterns in pattern sequence
→ relevant for auto running order selection mode

C41: Slider in % (maximum 80% possible)
→ determines how close the period of the grating is to the minimal possible value (I2), selected value is displayed on the right (relevant for auto running order selection mode)

### 6.3. Operating instructions

Running the software with default settings
1. Run the Labview VI ‘openSIM’
2. Select the available peripheral components
→ see appendix for information about possible peripheral components and corresponding differences in the user interface and operational instructions
→ do only select Z-actuator and EMCCD camera if you are sure that the appropriate components are connected
3. Select camera from the list of implemented cameras by clicking on the drop-down menu (C7) → select Andor iXon for Andor iXonUltra EMCCD camera
→ select Andor Zyla for Andor Zyla sCMOS camera
→ select Blank for testing purposes if no camera is connected
→ see appendix for information how to include an interface for a different camera

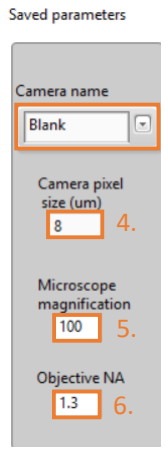
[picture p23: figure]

4. Insert camera pixel size in µm (C8) of selected camera
5. Insert magnification of used microscope objective (C9)
6. Insert NA of used microscope objective (C10)
7. Select ‘Imaging’ tab
8. Insert file name (C27)

3.

7.

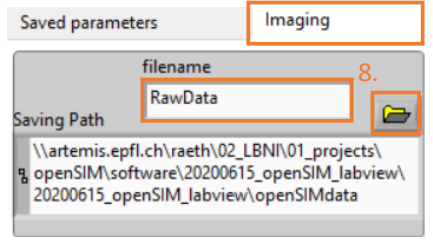
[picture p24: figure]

9.

2.

9. Select saving path (C28) (saving is enabled by default)
10. Select running order (pattern sequence) from list of running orders (C21) by clicking on the drop-down menu

→ naming scheme of running orders:
lines-p45-a4-N14
11. Set exposure time in seconds (C29)

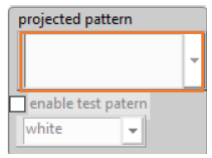
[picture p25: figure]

12. (optional) Enable binning if desired (C31) and select binning

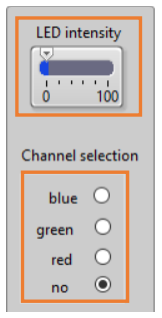
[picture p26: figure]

13. Set LED intensity in % (C36)
14. Select the LED channel (C37) to choose the color of the excitation light
15. Image acquisition (see instructions below)
16. Close the program by clicking stop button on front panel (C16)
→ Important to stop execution by stop button on front panel and not by ‘Abort Execution’ button in the LabView toolbar

Note:

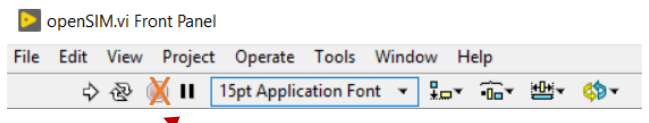
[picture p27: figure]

Repertoires (.repz file) have to be loaded only once to the SLM
→ Selecting repertoire path (C13) and sending repertoire path (C14) should be performed only when using the software for the first time after assembling the openSIM or if the user wants to load additional repertoires to the SLM
grating type | period of grating
number of angles | number of patterns

14.

15.

17.

! Do not stop the program here !

12.

13.

11.

Default settings
- Expert mode: disabled
- Test mode: disabled
- Repertoire path: to the file ‘all_patternSequences_4angles.repz’ in the directory containing the application
- Saving path: to folder ‘openSIMdata’ in the directory containing the application
- Saving: enabled (data is saved with the file ‘RawData’ at the default saving path)
- Fan: turned on
- Running order (pattern sequenc) selection mode: manual
- Test pattern: disabled
- EM gain: disabled

Acquire Data: widefield image
1. Adjust microscope focus to the desired imaging plane
2. Click on the ‘Widefield’ button (C18)

Acquire Data: SIM image
1. Adjust microscope focus (manually or via microscope interface) to the desired imaging plane
2. For timelapse imaging the timelapse imaging mode has to be enabled before next step (Clicking ‘SIM’ button acquires the first timelapse image, the subsequent images are acquired in a sequence defines by C34 and C35)
3. Click on the ‘SIM’ button to acquire a SIM image stack (C19)

Manual z-stacking
→ stacking disabled: one single SIM/widefield image is acquired → stacking enabled: several SIM/widefield images are acquired
1. Enable z-stacking
2. Select manual z-stacking mode
3. Select the number of desired images within the stack
4. Manually select the starting z-position of the microscope objective
5. Click either the Widefield (C18) or the SIM button (C19) depending on the desired imaging mode in order to start the acquisition
6. After every acquired image, a dialog window pops up asking if the next image can be acquired. Before clicking on acquire, change manually the z-position of the objective by using the focus adjustment knob of the microscope. When clicking acquire, the next image will be acquired
7. Repeat step six until all images are acquired

1.

3.

2.

## 7. Data handling

- The acquired data is saved in the selected folder (file name can be seleted with C27, path of folder where data is saved in can be selected with C28 and is shown in I6)
- The data is saved in tiff format (widefield: tiff file with one frame, SIM: tiff file with image stack where the number of frames corresponds to the chosen number of patterns in pattern sequence (shown in I18)
- Along with the tiff image file, the repertoire (repz file with single running order) corresponding to the used running order (pattern sequence) selected with C21 and a file containing the metadata (.txt) (same file name as image file but different file format) is saved
- The metadata file contains information about the used parameters during the image acquisition (e.g., image type, pixel size, number of patterns, LED channel, exposure time)
- The tiff format is a commonly used file format (lossless file format) compatible with ImageJ and the image reconstruction software SIMToolbox (MATLAB toolbox for structured illumination fluorescence microscopy)

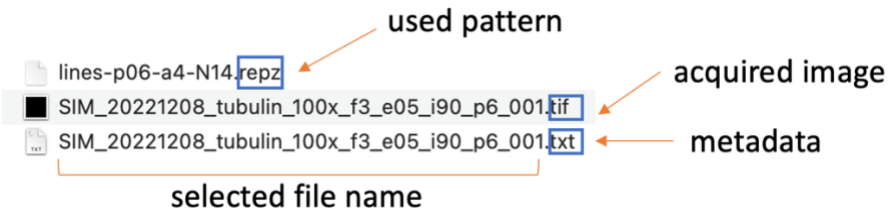
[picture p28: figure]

Example how data is saved during image acquisition

## 8. Troubleshooting

Problem | Possible reason | Possible Solution
When first running the openSIM software, it is not possible to connect to the SLM | The openSIM software might encounter problems connecting to the SLM due to missing drivers | Download the openSIM software file from here (https://zenodo.org/records/10067217) and extract it on your local drive. Try to run the openSIM software from this file.
It is not possible to connect to the NI DAQ, SLM or camera → error message(s), indicator does not light green and software automatically stops execution) → if the openSIM software cannot establish the communication with the SLM and/or DAQ, camera an automatic error message will appear and the | The openSIM software was closed by clicking the ‘Abort execution’ at the Labview toolbar instead of clicking the stop bottom (C16). By clicking the user interface stop bottom it is assured that the NI DAQ, SLM and camera are set back to their default settings and that the devices are closed properly. Not doing so can lead to reconnection problems when subsequently restarting the software. | Close the complete openSIM LabView project and reopen. If this does not solve the problem close the software and dis- and reconnect the individual components. Then start the applications again. If it is still not possible to connect to the devices, close the applications and restart the computer.

software execution is
stopped
Error message: ‘Error 5006 occurred at AT Open A.vi: OUT OF RANGE’ | Camera is physically not connected to the PC | Connect the Andor Zyla camera to the PC via the USB cable
| The openSIM software cannot connect to the camera. This problem can occur if the ‘Abort execution’ at the Labview toolbar is used for stopping the program execution instead of the stop button in the user interface (C16). If the camera is not closed properly, the data structures which are held internally by the SDK are not cleaned up which can lead to problems when reconnecting to the camera. | Disconnect and reconnect the USB cable from the camera to the PC. If this does not solve the problem restart the camera first and if the error message still occurs, then also restart the PC. One can also check if the camera can be accessed via via AndorSolis (Andor’s camera control system)
When enabling z-stacking error message appears | Z-actuator at peripheral component selection is not enabled (C6) | Enable z-actuator and try to enable z-stacking again

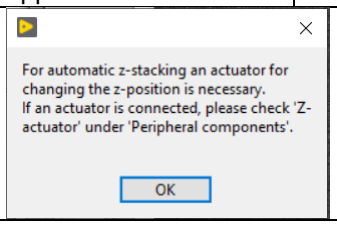
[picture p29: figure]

## 9. Software adaptation

### 9.1. Integration of a different camera

The current version of the software includes an integration for an Andor Zyla sCMOS, an Andor iXon EMCCD camera. In order to integrate another camera to the openSIM software the subVIs listed below have to be adapted. All of these VIs contain a main case structure to differentiate between the implemented cameras. An additional case has to be added to include the necessary code within the subVIs. The camera name has to be added to the Combo Box Camera name to select the corresponding case in the subVIs. Many scientific camera manufacturers provide Labview SDKs for their camera systems which are often structured as libraries containing several subVIs to control the camera. The exact integration of the camera highly depends on the camera type and the camera manufacturer. In the section below the general approach how to implement a different camera into the openSIM software is descripted. For more specific information about the camera-specific SDK please see the information provided by the manufacturer. They are often distributed together with the SDK installation program or accessible online.

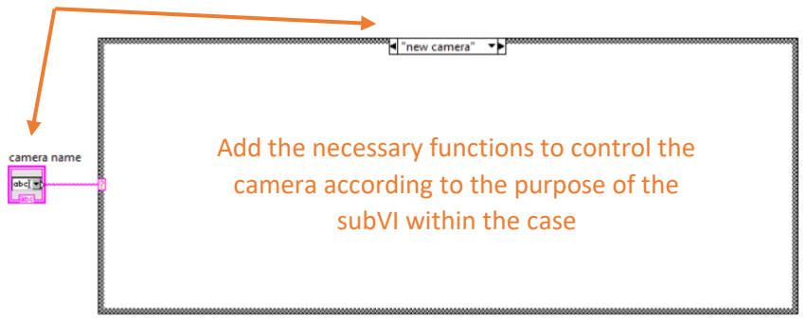
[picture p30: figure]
camera according to the purpose of the subVI within the case

subVi_Initialyse_Camera
- input: Camera name, Em gain enable, Em gain, Exp Time, binning enable, binning size
- output: camera connected?, IMAQ Buffer, Handle, Xpixel, Ypixel

→ in this subVI, the camera/camera specific library has to be initialized and all general and camera specific parameters have to be set in order to run the camera (for more specific information about the camera initialization and the necessary parameters please refer to the information about the corresponding SDK often provided by the camera manufacturer)
→ the indicator camera connected? has to be set true at the end of the subVI if everything was initialized and set correctly
→ EM gain only relevant for EMCCD cameras
→ handle, area of interest (AOI) width, AOI height, Auxiliary (AUX) output source (configures the signal which appears on the AUX output pin of the camera) is relevant when using SDK3 to control sCMOS cameras from Andor

Internal settings for Andor Zyla 4.2 sCMOS camera:
- Pre-amplification gain control: 12-bit (low noise)
- Auxiliary output source: Fire all
- AOI height: 1048px, AOI width: 1048px

Internal settings for Andor iXonUltra EMCCD camera:
- EM gain mode: 8-bit
- Acquisition mode: 1
- Read mode: 4
- Trigger mode: internal
- Acquisition timing: TTL high
- Shutter: auto

EM_gain_enable
- input: EM gain, Handle, Camera name, EM gain enable
→ only relevant when using a EMCCD camera
→ if EM gain is enabled the value for the EM gain has to be set to the value determined by C44

sub_vi_exp_time
- input: Handle, Camera name, Exp time
→ in this subVI the exposure time of camera in seconds has to be set to the value determined

Add a new case to the structure which is selected by the camera name

Add the necessary functions to control the

by C29

subVI_GetImage_Camera
- input: Camera name, IMAQ buffer, Handle, Xpixel, Ypixel
- output: array, array 2D, Display 2
→ in this subVI, the image acquisition has to be implemented including triggering start of image acquisition by the camera, readout data from camera, if necessary, caching in an additional buffer, conversion of byte data into pixel data according to the selected pixel encoding
→ Xpixel / Ypixel are used to create 2D array of pixel data to save the data afterwards (saving has not to be included in the subVI)
→ IMAQ buffer is used to display data

subVI_Close_CamerasubVI_Close_Camera
- input: Camera name, Handle
→ closes camera
→ within the subVI it has to be ensured that the camera is closed properly to ensure a bugless start at the next execution (for many cameras the data structures which are held internally by the SDK have to be not cleaned up)

### 9.2. Integration of a different focus positioning

The implemented z-stacking/single z-movement uses an analog signal via the DAQ device to control a piezo focus positioner (piezo focus positioner Jena Mipos 100 from Piezosystem). The piezo focus lens positioner can move objectives in a precise and accurate way. To do so, the piezo positioner is attached to the standard optical microscope. The objective is then screwed into the piezo positioner instead of the objective turret. In order to use a piezo focus positioner with a different motion range or voltage range but with the same operation principle (see figure 1), the initialization values for the motion and voltage range has to be changed in the initialization frame (first frame in Labview block diagram). If a different actuator type or a different operating principle should be implemented, the subVI subVI_Zstacking_piezo and the cases within the consumer loop have to be changed. Corresponding cases are Z-auto, stacking_off, checking stacking input, single z-movement_on, single z-movement_off.

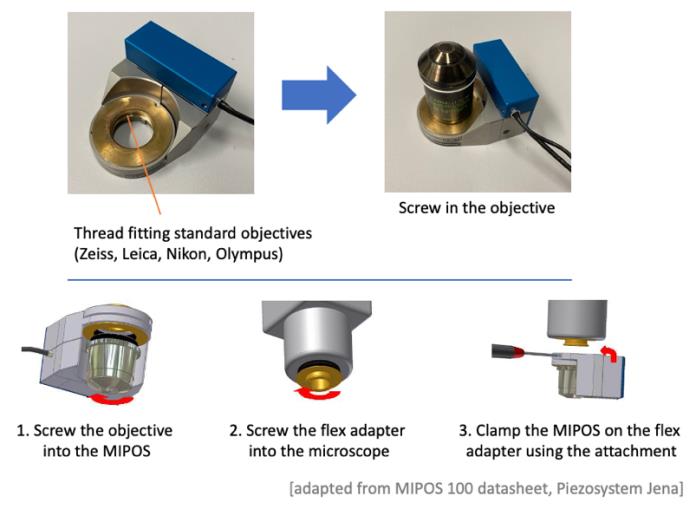
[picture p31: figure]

## Appendix

Installation of Andor SDK3 for LabView
→ LabView has to be installed before installing SDK3 for LabView
1. Run the Andor SDK3 for LabView installer (the SDK can be downloaded at https://andor.oxinst.com/products/software-development-kit/software-development-kit if it is not provided when purchasing the camera)
2. Choose the folder where LabView is installed as folder to install the SDK3 (program files → National Instruments → LabView XXXX) - if several LabView applications are installed (version, application bitness), make sure that the correct one is chosen
→ e.g. C:\Program Files\National Instruments\LabVIEW 20xx
→ e.g. C:\Program Files (x86)\National Instruments\LabVIEW 20xx
→ or corresponding path to the program folder for other operating systems than windows

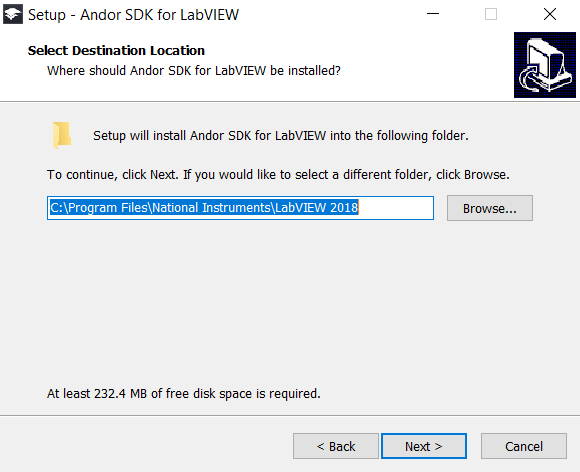
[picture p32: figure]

Status / log information

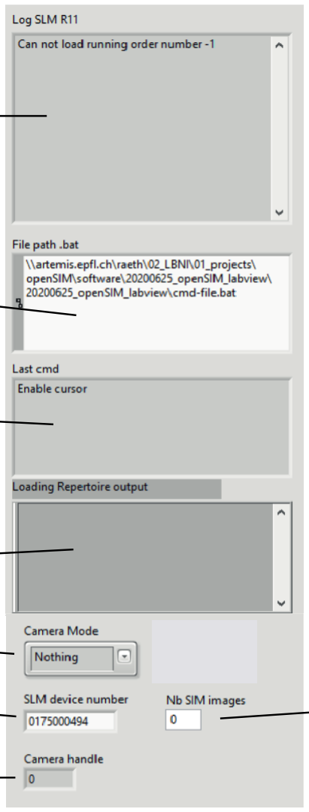
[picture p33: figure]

Figure 1: User interface with status / log information

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
I11: Dislaying current status of SLM
I12: Path to bat le
I13: Last executed command
I14: Text which is passed to command line I15: Current acquistion mode
I16: Device number of SLM
I17: Handle of camera
I18: Number of projected patterns

ADDITIONAL INDICATORS:

I11: Display showing the current status of the SLM R11
→ e.g. bat file cleared/loaded, repertoire loaded, load running order number, cannot load running order number, pattern send, device closed

I12: File path to bat file
→ the bat file contains commands for the SLM in order to load the repertoire
→ see I4 for more information about the repertoire
→ the path should not be changed from the default value.

I13: Display showing the last executed command in the openSIM program

I14: Display showing the text which is passed to the command line in order to run a system command sent to the SLM (bat file to load repertoire)

I15: Current acquisition mode (i.e. video, widefield, SIM)
→ selection via controls C17 (for video), C18 (for widefield), C19 (for SIM)
→ video: mainly for test purpose, continuous acquisition of widefield images,
without a saving option
→ widefield: acquisition mode for widefield imaging, default: one image is acquired when clicking C18, number of acquired images depends on number of stacks (C25)
if z-stacking is enabled
→ SIM: acquisition mode for SIM imaging, number of total images depends on number of patterns in pattern sequence (I17) and number of stacks (C25) if z-stacking is enabled

I16: Device number of connected SLM

I17: Handle to connected camera (relevant for sCMOS camera Andor Zyla)

I18: Number of SIM images/patterns
→ is automatically indicated based on the chosen running order (pattern sequence)

Automatic z-positioning

This section applies only if the piezo focus positioner Jena Mipos 100 (Piezosystem) is used according to the operating principle depicted in figure 5. If a piezo positioner with a different motion and voltage range or a different actuator type is used, please refer to the section 5 for more information about the integration.

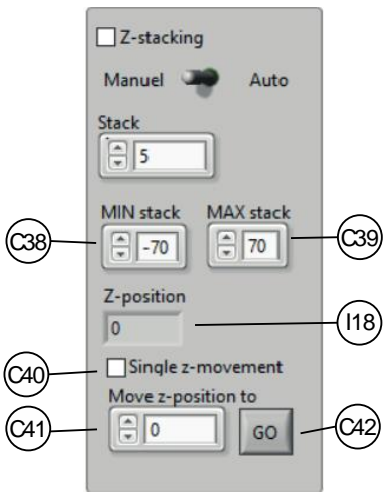
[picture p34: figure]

Figure 2: User interface for automatic z-stacking

ADDITIONAL INDICATOR AND CONTROLS

I16: Current position of z-actuator in µm during z-stacking if z-stacking is enabled

C38/C39: stack range in µm
→ min: z-position of first stack relative to mid-position
→ max: z-position of last stack relative to mid-position
(values have to be within motion range of z-actuator, for MIPOS 100 -70µm – 70µm)

C40: Enabling/disabling single adjustment of z-position by z-actuator
→ if enabled, piezo focus positioner is set to mid-position as initial position (half of its motion range)
C43 | C44

C38: Motion range of z-actuator (min)
C39: Motion range of z-actuator (max)
C40: Enabling single z-movement
C41: Desired z-position within motion range of z-actuator C42: Start single z-movement

I18: current z-position of acutuator during z-stacking

C43: Enable EM gain for EMCCD camera C44: Set EM gain for EMCCD camera

C41 Desired z-position for single z-movement
→ focus positioner moves to inserted z-position in µm relative to mid-position by clicking the GO button (value has to be within motion range of piezo focus positioner, for MIPOS 100 -70µm – 70µm)

C42: Executing single z-movement

OPERATIONAL INSTRUCTIONS FOR AUTOMATIC Z-POSITIONING

Z-stacking:
→ relative to mid-position (half of the piezo motion range), mid-position is used as initial position
1. Enable z-stacking (C23) → piezo is set to mid-position (order important!)
2. Adjust microscope focus (manually or via microscope interface) to the object of interest
3. Set stack size (C25)
4. Set z-position of first stack in µm relative to mid-position
(value has to be within motion range of piezo z-positioner) (C38)
5. Set z-position of last stack in µm relative to mid-position
(value has to be within motion range of piezo z-positioner) (C39)
6. Acquire either widefield or SIM images

Single z-movement:

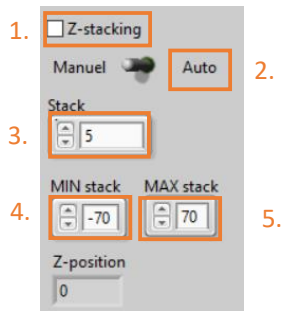
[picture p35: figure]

→ relative to mid-position (half of the piezo motion range), mid-position is used as initial position
→ independent of z-stacking: if z-stacking is enabled, the piezo focus positioner will be set back to its initial mid-position
1. Enable focus adjustment (C40) → piezo is set to mid-position (order important!)
2. Adjust microscope focus to the object of interest
3. Set desired z-position in µm relative to mid-position (C41)
4. Click the GO button (C42) to change z-position

3.
4.

1.

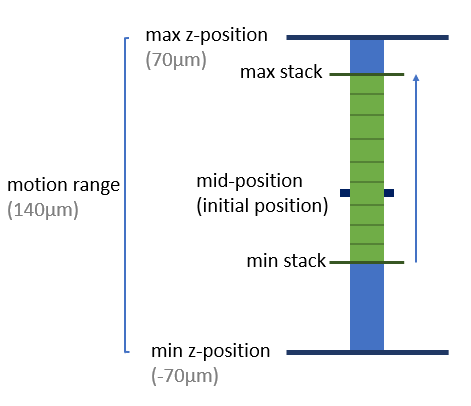
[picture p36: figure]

Figure 3: Schematic illustrating z-stacking via piezo focus positioner

EMCCD camera

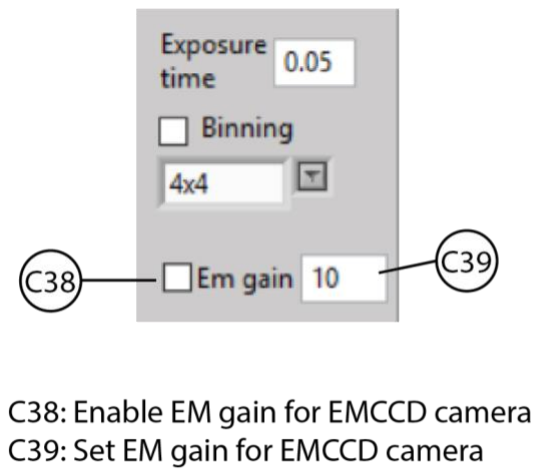
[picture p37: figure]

Figure 4: User interface for EMCCD cameras

Additional controls
C38: Enabling/Disabling electron multiplying (EM) gain of EMCCD
→ if EM gain is enabled, the gain is set according to the value specified with C39 → if EM gain is disabled, the gain is set to zero

C39: EM gain

Troubleshooting Andor Zyla integration:

Problem | Possible reason | Possible Solution
Error message: ‘Error 5006 occurred at AT Open A.vi: OUT OF RANGE’ | Camera is physically not connected to the PC | Connect the Andor Zyla camera to the PC via the USB cable
| The openSIM software cannot connect to the camera. This problem can occur if the ‘Abort execution’ at the Labview toolbar is used for stopping the program execution instead of the stop button in the user interface (C16). If the camera is not closed properly, the data structures which are held internally by the SDK are not cleaned up which can lead to problems when reconnecting to the camera. | Disconnect and reconnect the USB cable from the camera to the PC. If this does not solve the problem restart the camera first and if the error message still occurs, then also restart the PC. One can also check if the camera can be accessed via via AndorSolis (Andor’s camera control system)

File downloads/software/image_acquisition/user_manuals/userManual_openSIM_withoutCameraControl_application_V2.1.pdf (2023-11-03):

# User manual openSIM software

# software version: without integrated camera control

## Contents

## 1. Introduction to the openSIM software

The openSIM software is written with LabView 2018. It controls the openSIM add-on and openSIM interface box including LEDs, data acquisition device (DAQ), spatial light modulator (SLM) and temperature control. It comprises of a user interface to enter the necessary parameters, execute commands and to display currently used parameters, executed commands and error messages. Additionally, it can optionally interface additional peripheral components such as a piezo focus positioner, if available.
The main functionalities of the openSIM software are controlling the LEDs (channel selection, intensity), selecting the pattern sequence projected by the spatial light modulator (SLM), actuating the fan and handling the metadata storage. The projected patterns can be selected either manually from a list of patterns or automatically based on parameter inputs from the user. The software saves the used parameters and the used projected pattern sequence the facilitate the image reconstruction. If a device necessary for z-stacking, such as a piezo focus positioner or a motorized focus controller, is available, the software can be used to perform z-stacking. The z-stacking function automatically changes the focus of the objective by providing an analog output to the focus adjusting device.

Difference to software versions with integrated camera control:
It is important to note that there are distinct differences between the software version without integrated camera control (described here in the user manual) compared to the software versions with integrated camera control.
This software version (software version without integrated camera control) is an executable (stand-alone application) which can be distributed without needing the full LabView development version for which a chargeable license is needed. In order run a LabView executable the free LabView Runtime Engine corresponding to the LabView version with which the application was developed is sufficient. To avoid the need of deployment licenses for LabView modules (some are subject to charges) we only integrated LabView modules into the openSIM software for which the software drivers are free of charge.
In this software version, we intentionally did not integrate the camera control into the openSIM software in order to avoid the need for chargeable and camera-specific SDK (e.g. SDK 3 LabView for control of Andor Zyla, iXon camera). This requires the parallel use of the camera control software (for image acquisition) and the openSIM software (for control of the openSIM add-on and interface box). As the imaging data handling (such as displaying and saving acquired image) is linked to the image acquisition, this functionality was removed from this software version is should be handled by the camera software. Besides avoiding the need of chargeable licenses, this openSIM software version has the advantage of being completely independent of the used camera type or manufacturer whereas a software with integrated camera control is inherently camera specific.
The openSIM application in combination with the camera software of the used camera, fulfills the same functionalities than the other software versions.

## 2. Structure of user manual

- The main part of the user interface describes operating the openSIM software using the default settings.
- The appendix contains description of the control of peripheral components, the automatic pattern selection mode and the optional display of status and log information.
- The user interface is categorized in controls (user can enter information, execute commands; indicated with C) and indicators (information are displayed to the user, indicated with I)

## 3. Installation

→ for none of the software which are required to be installed in order to run this openSIM software version (without camera control) a chargeable key/license is required

### 1. Microsoft Visual Studio:

Install Microsoft Visual Studio Express 2013. You may encounter compatibility issues if you attempt to run the openSIM software with a different version of Visual Studio. A key is not required for the installation of the Express version.
Download: https://visualstudio.microsoft.com/vs/older-downloads/

This will download an ISO file. To access to setup.exe file in order to install the software you can either mount (right-click on ISO file → mount command) the file (opens a virtual drive that is visible in the file explorer) or extract the files (right-click on ISO file → extract)

### 2. LabView

Install the LabView runtime engine 2018 SP1. The openSIM software was created with LabView 2018 SP1. The version of the runtime engine has to be the same than the LabView version used to create the application.
Download: https://www.ni.com/en/support/downloads/software-products/download.labview-runtime.html#484336 (https://www.ni.com/en/support/downloads/software-products/download.labview-runtime.html#484336)

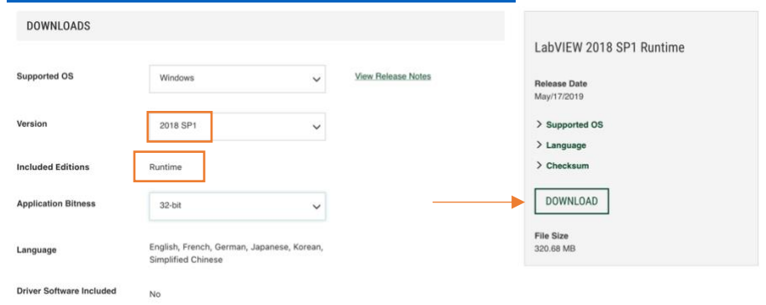
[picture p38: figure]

Install the NI-DAQmx 18.6 driver software.
Download: https://www.ni.com/en/support/downloads/drivers/download.ni-daqmx.html#291872 (https://www.ni.com/en/support/downloads/drivers/download.ni-daq-mx.html#291872)

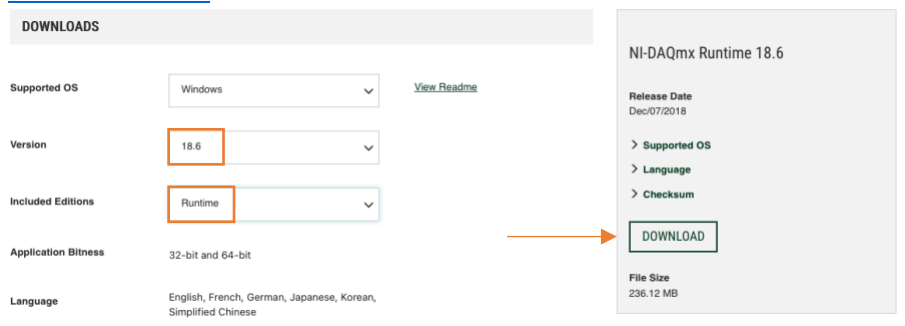
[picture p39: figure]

(If you already have NI Package Manager installed, both LabView runtime engine and NI-DAQmx can be also directly installed there. For more information see: https://knowledge.ni.com/KnowledgeArticleDetails?id=kA03q000000YGvpCAG&l=en-CH)

### 3. MetroCon 3.3

Install the MetroCon 3.3 application from …\drivers\ForthDD_QXGA\MetroCon within the distributed openSIM software folder
Check that MetroCon is installed in C:\Program Files…

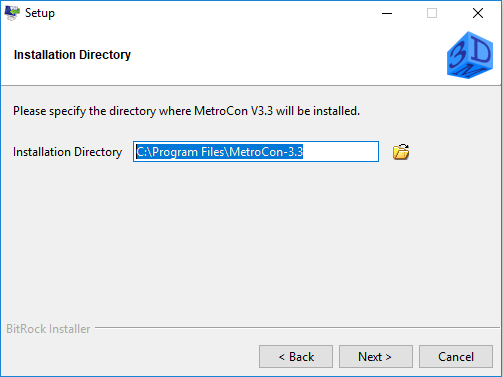
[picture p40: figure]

Install ATMEL Corps. Ports (COM & LPT) (if the window pops up)

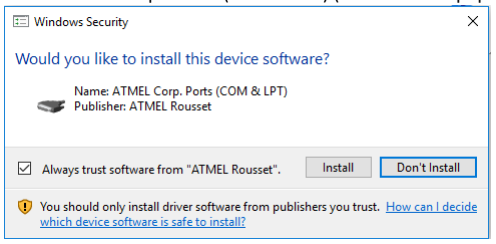
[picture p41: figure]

4. Restart the computer after the installation steps
5. Copy the openSIM software folder to a local directory and make sure that the folder structure looks like below

## 4. Distributed files and required folder structure

These are the distributed files in order to run the openSIM application (software version without camera control).

Please ensure that the folder structure is retained when copying the distributed openSIM folder to your local directory as the openSIM software used this folder structure as base directory.

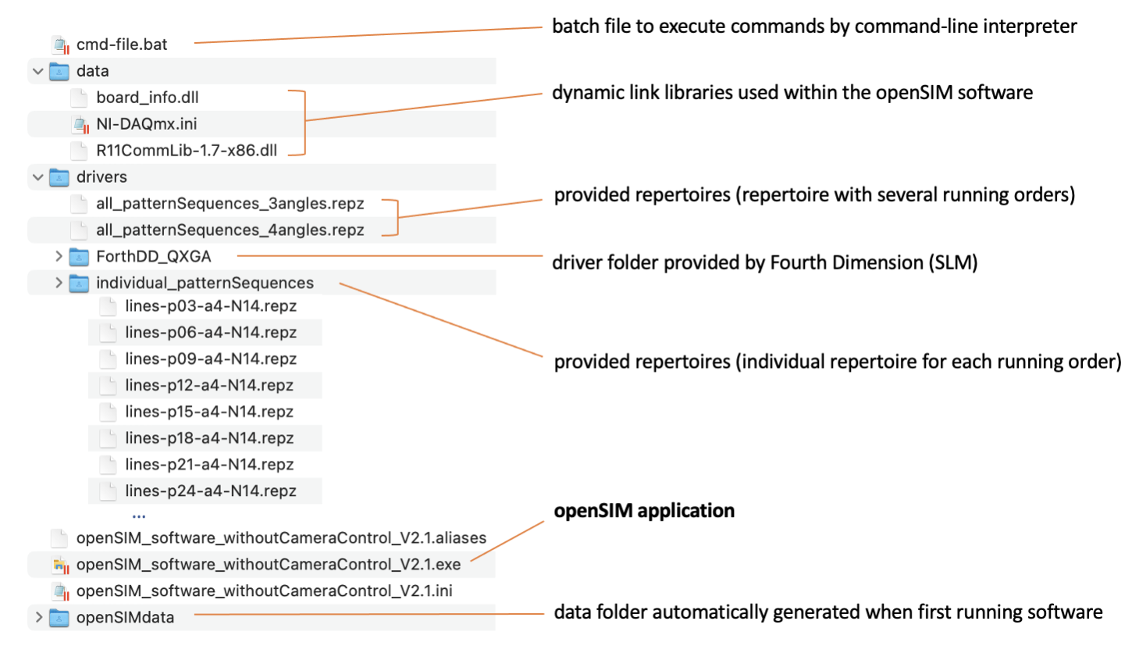
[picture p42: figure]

## 5. Illumination patterns

For SIM image reconstruction, the sample needs to be illuminated with a set of patterns with different phases and angles. We generated different line illumination patterns (according to SIMToolbox – supplementary documentation and user’s guide) which are distributed with the openSIM software. For a better understanding we provide here some background information and explain the used terminology.

Pattern sequence:
- sequence of patterns projected by the SLM during the SIM image acquisition
- each pattern of the sequence has a different phase and angle → the number of patterns in the sequence defines the total number of images during one SIM image acquisition (one image is acquired per pattern and the total amount of images is saved as an image stack)
- pattern sequence is stored as repertoire (.repz file format), a zip file containing:
- images of the pattern (.bmp file format)
- timing schedule (.seq file format, supplied by Forth Dimension, defines the bright and dark phases of the SLM)
- running order (.rep file format, describes the order of the projected pattern images in the sequence and the and trigger mode)
- a pattern sequence can contain several running orders (rep file with description of several running orders)
- we provide the generated pattern sequences in two ways:
- repertoire with several running orders (repz files: all_patternSequences_3angles.repz; all_patternSequences_4angles.repz): repertoire to be uploaded to the SLM, the running orders define the different available individual sequences of pattern which can be projected by the SLM
- repertoire with one running order: when using the SIMToolbox for SIM image reconstruction, the software requires information about the pattern sequence projected during the SIM image acquisition, the software can automatically read in the pattern information when stored in a specifically formatted text file (.yaml file format)
→ to facilitate the automatic read in of the pattern description file, we provide a folder (individual_patternSequences) which contains an individual repertoire (repz files: lines-p03-a4-N14.repz, ….) for each running order (lines-p03-a4-N14,…) available in the provided repertoires descripted above (all_patternSequences_3angles.repz; all_patternSequences_4angles.repz), when acquiring a SIM image the individual repertoire corresponding to the used running order is saved together with the acquired data

Terminology for openSIM user interface and user manual:
→ for a better differentiation we use the term ‘repertoire’ for .repz files and the term ‘pattern sequence’ for the actually, by the running order defined and by the SLM projected, sequence of patterns during a single SIM image acquisition

## 6. Control of the openSIM software with default parameter

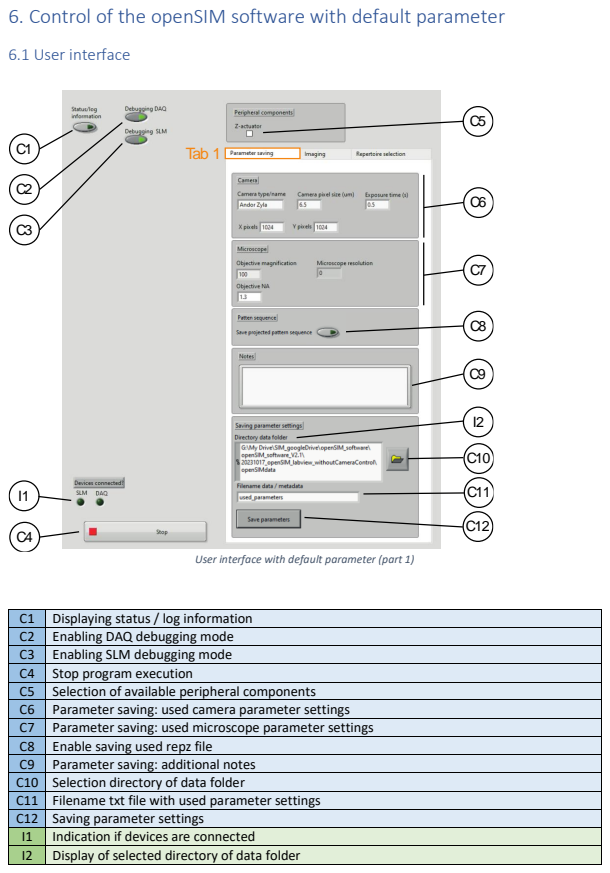
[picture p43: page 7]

User interface with default parameter (part 1)

C1 | Displaying status / log information
C2 | Enabling DAQ debugging mode
C3 | Enabling SLM debugging mode
C4 | Stop program execution
C5 | Selection of available peripheral components
C6 | Parameter saving: used camera parameter settings
C7 | Parameter saving: used microscope parameter settings
C8 | Enable saving used repz file
C9 | Parameter saving: additional notes
C10 | Selection directory of data folder
C11 | Filename txt file with used parameter settings
C12 | Saving parameter settings
I1 | Indication if devices are connected
I2 | Display of selected directory of data folder

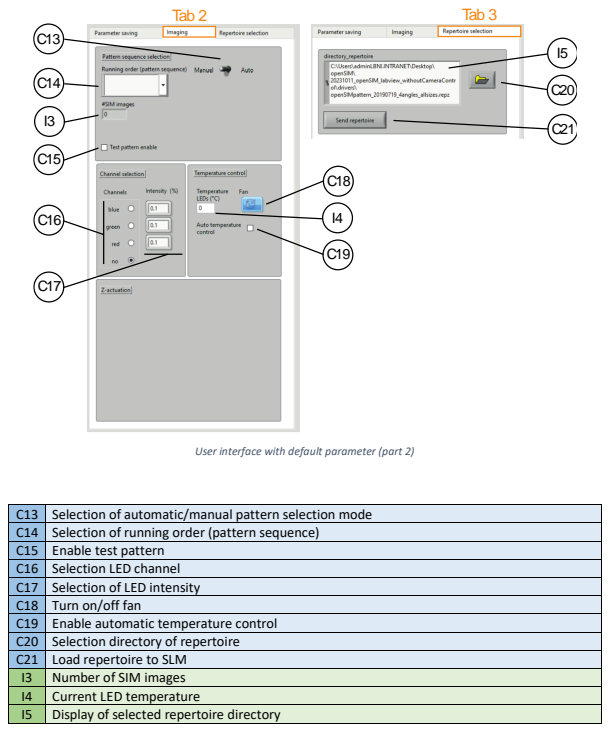
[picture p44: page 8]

User interface with default parameter (part 2)

C13 | Selection of automatic/manual pattern selection mode
C14 | Selection of running order (pattern sequence)
C15 | Enable test pattern
C16 | Selection LED channel
C17 | Selection of LED intensity
C18 | Turn on/off fan
C19 | Enable automatic temperature control
C20 | Selection directory of repertoire
C21 | Load repertoire to SLM
I3 | Number of SIM images
I4 | Current LED temperature
I5 | Display of selected repertoire directory

### 6.2 Input parameters

→ This section covers only the indicators and controls for the operation mode with default settings → For information about the additional indicators and control see the appendix
→ Depending on certain selections/modes some of the indicators and controls are not visible or greyed out. These controls and indicators become visible and enabled when the corresponding mode is selected.

INDICATORS:

I1: Indicator showing if devices (SLM, DAQ) are connected
→ indicator is green if the communication between the openSIM software and the devices is established

I2: Display of the selected directory of data folder
→ shows the path to the data folder
→ folder can be selected/changed with C10

I3: Number of SIM images
→ number of SIM images based on selected running order (C14)
→ corresponds to the number of patterns in the selected set of patterns and thus the number of images which need to be acquired during the SIM image acquisition

I4: Temperature measured by thermistor at illumination block holding the LEDs
→ temperature is used as input for the temperature control system
→ if the temperature is too high, the two fans at the aluminum heat sink extender are turned on

I5: Display of selected repertoire directory
→ directory selected with C20

CONTROLS:

C1: Enabling/disabling displaying of status and log information
→ this mode includes additional indicators which support debugging
→ see appendix for more information about the indicators

Debugging modes:
- In order to facilitate testing and debugging of the software and the individual devices (i.e. SLM, NI DAQ) it can be useful to connect only some of the devices (e.g. only NI DAQ is connected and tested with the software, while the SLM is not connected). However, in the default (non-debugging) mode the openSIM software will return an error message and stops when devices are not connected (e.g. because of missing device handles when the device is not connected which are needed in the initialization step). In the debugging mode, the software can be used despite the corresponding device not being connected.
- Debugging mode can be used for only one device or several devices at the same time
- In debugging mode the software does not try to establish a connection to the devices (SLM, DAQ) and device depended functions (e.g. DAQ: change channel, SLM: change running order are not executed)

C2: DAQ debugging mode
→ facilitates the testing of functions independent of the DAQ devise
→ if enabled, the software does not try to connect to the DAQ device, software can be used even if the NI DAQ is not connected

C3: SLM debugging mode
→ facilitates the testing of functions independent of the SLM devise

→ if enabled, the software does not try to connect to the SLM device, software can be used even if the SLM is not connected

C4: Stop button to end the program execution
→ the program has to be stopped here and not with the button in the LabView task line (otherwise devices such as SLM and DAQ are not closed properly and some parameters settings are not set back correctly)

C5: Selecting available peripheral component (Z-actuator)
→ specific controls are visible/invisible depending on the availability of the corresponding peripheral component
→ Z-actuator: can be selected if an actuator for changing the z-position of the objective such
as a piezo focus positioner is available and implemented (see appendix for more information about the parameter settings and use of automated z-positioning)

Tab1: Parameter saving
- This tab handles the saving of the used parameter settings during image acquisition.
- The information entered here are saved in a txt file and the used .repz file is saved in addition on request. The saved txt file with the parameter description and the .repz file enables the automatic import of information, necessary for the image reconstruction by the SIMToolbox. The txt and repz file structure is created in a way to be compatible with the automatic SIMToolbox reading in of parameter settings.
- The txt file can save additional information which can be useful as metadata of the imaging data.

C6: Used camera parameter settings
- camera type/name
- camera pixel size in µm
- exposure time in seconds
- X and Y camera pixels
→ see the specification sheet of your camera for the corresponding information

C7: Used microscope parameter settings
- magnification of used objective
- NA of used objective
- Microscope resolution (calculated resolution in µm, based on wavelength of selected channel and NA of objective)

C8: Enable/Disable saving of used repz file
→ if enabled the repz file corresponding to the used pattern selected with C14 is saved in the same folder than the txt file
→ only relevant for SIM image acquisition

C9: Additional notes
→ additional notes added to the txt file together with the parameter settings

C10: Selection directory of data folder
→ default: folder ‘openSIMdata’ in same directory than openSIM software
→ when using the openSIM software for the first time ‘openSIMdata’ folder is generated automatically

C11: Filename of txt file containing the parameter settings used during image acquisition
→ acquired image via camera software (tiff file) has to have same file name as txt file for automatic upload of metadata by SIMToolbox

C12: Saving parameter settings
→ the values from C6, C7, C9 are saved in a txt file with the filename defined by C11

→ when save button clicked a new folder in the directory of the data folder (I2) is generated with the corresponding date as filename
→ within this folder the txt file is saved with the file name selected with C10
→ if C8 is enabled also the used .repz file is saved in this folder

Tab 2: Imaging

C13: Selection of automatic/manual running order (pattern sequence) selection mode
→ manual running order selection mode: the user manually selects the running order (pattern sequence) from the list of running orders available for the uploaded repertoire in the dropdown menu (default)
→ auto running order selection mode: the running order (pattern sequence) is automatically selected based on certain input parameter (see appendix for more information about the automatic running order selection mode)

C14: Selection of running order (pattern sequence)
→ selection from a list of all running orders which are available in the repertoire currently uploaded onto the SLM
→ selected running order defines the pattern sequences actually projected by the SLM

C15: Enabling/Disabling test pattern
→ the test pattern are static patterns which can be used for testing purposes
→ video acquisition mode in camera software should be selected for testing
→ if test pattern is enabled, the control with the list of available test pattern will be displayed
→ different projected test patterns can be selected available test pattern: white, black, bars1, bars2 (pattern with vertical lines), default: test pattern disabled

C16: Selection LED channel
→ color of excitation light (blue, green, red LED)
→ default: no LED selected

C17: Selection of LED intensity
→ LED intensity in %

C18: Manually turning on/off the two fans for LED cooling
→ can be automatically controlled when enabling automatic temperature control (C19)
→ fans support the cooling of the LED which are mounted onto an aluminum heat sink extender

C19: Enabling automatic temperature control
→ if the heat sensor at the heat sink measures a temperature above 30°C the fans are turned on and if the temperature falls below 30°C the fans are turned off

C20: Selection of directory of repertoire
→ directory to repertoire in order to send/upload onto SLM

Tab 3: Repertoire selection
→ the repertoire can also be selected and uploaded to the SLM via the MetroCon software

C13: Browse directory to select file path to the repertoires
→ selected .repz file which is loaded to the SLM
→ default: all_repz_files_20190719_4angles_allsizes.repz (distributed in driver folder in the directory containing the application; directory of repz file should not be changed)

C14: Sending repertoire to SLM
→ uploads the repertoire selected with C13 and displayed at I5 onto the SLM
→ repertoire has to be sent to SLM only once, afterwards it is uploaded onto SLM
→ sending repertoire has to be done only when using the SLM for the first time or when wishing to change the current repertoire

### 6.3 Operating instructions

Running the software with default settings

Start the openSIM software
1. Execute the openSIM software application (openSIM_software_withoutCameraControl_V2_1.exe)
2. Select the software mode
→ right after the software user interface opens a window opens in which the software mode (either normal mode or debugging mode) has to be selected
→ default: normal mode (see section 4.1 for more information about the debugging mode)

Debugging software mode:
→ communication to DAQ and/or SLM is not established
→ debugging mode for either one or both devices can be selected

Normal software mode:

Enter and save the used parameter settings

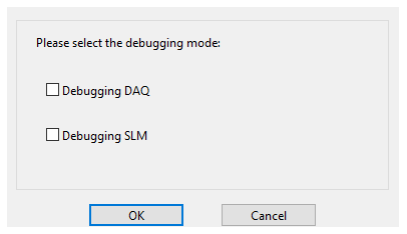
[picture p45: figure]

3. Insert the used parameter settings (C6, C7, C9) in the fields under ‘Parameter saving’ (tab 1) based on the microscope and objective used for the image acquisition session
→ the fields camera pixel size, x/y pixel, objective magnification are mandatory information needed for the correct image reconstruction, the other fields are optional
4. If the data should be saved in another folder than the default directory ‘openSIMdata’, the directory can be changed with C20
5. If another file name for the txt file with the metadata than the default ‘used_parameter’ is wished for, the filename can be changed with C11
6. Select the running order in order to define the pattern sequence is going to be projected during the SIM image acquisition in the drop-down menu C14 under ‘Imaging’ (tab 2); the corresponding number of images which need to be acquired during the SIM image acquisition is displayed in I3

→ naming scheme of running order:
lines-p45-a4-N14
7. click C12 to create the data folder for this imaging session and save the used parameter and projected pattern in the generated folder
pattern type | period of grating
number of angles | number of patterns

Set LED channel settings
8. Select the desired LED channel based on the used fluorophore (C16)
9. Set the desired intensity of the corresponding channel (C17)

Start the camera software
→ we used the Andor control software Solis in parallel to the openSIM software → parameters specific to the used camera software are indicated in grey
10. Start the control software of the corresponding camera in use
→ Andor Solis
11. Arrange the openSIM software and camera software next to each other

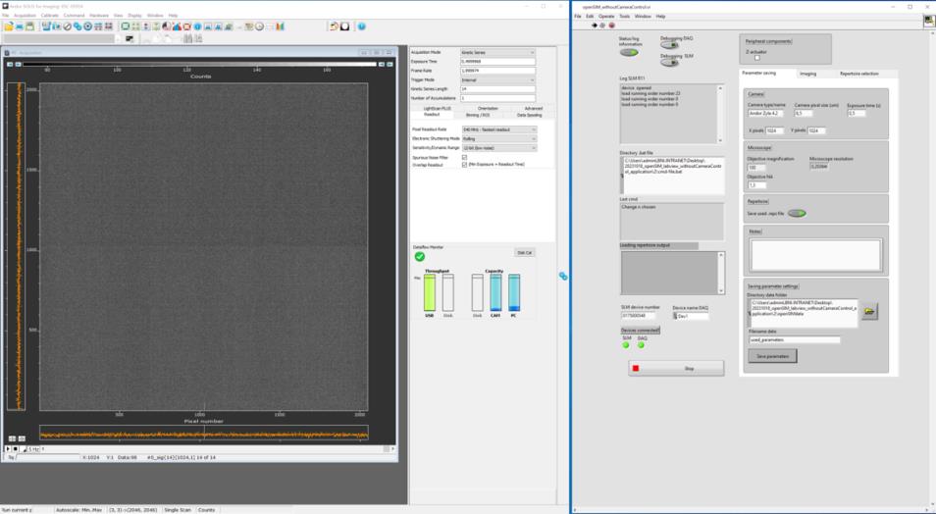
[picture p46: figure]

Select the camera parameters
10. Select the triggering mode
→ ‘Hardware’ → ‘Auxiliary Output Configuration’ → ‘Fire all’
11. Select the data folder generated in step 6 as imaging data directory → ‘Acquisition Setup’
12. Change the image file name to the file name used for the txt file (C11)
→ ‘Acquisition Setup’
12. Change the acquisition type from acquisition of a single image to acquisition of a series of images (series/stack of subsequent images saved as one file)
→ ‘Acquisition Setup’ → ‘Acquisition mode’ → ‘Kinetic series’
13. Set the image series length (amount of subsequently acquired images) according to the selected projected set of patterns (I3)
→ ‘Acquisition Setup’ → ‘Kinetic series length’ → insert same number as number of SIM images
14. Set desired exposure time
→ ‘Acquisition Setup’ → ‘Exposure time’
15. Acquire a series of SIM images
→ ‘Take Signal’

Acquisition setup

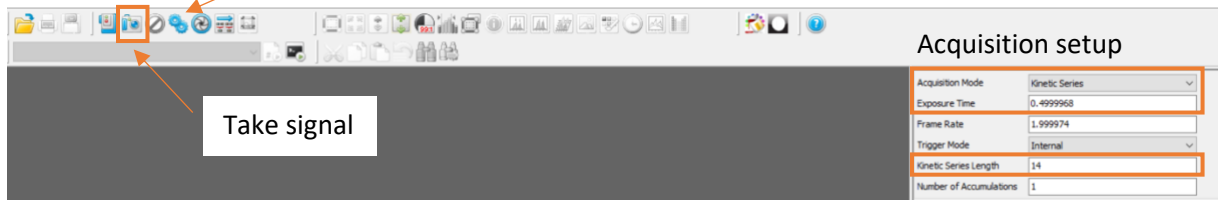
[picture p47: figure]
Take signal; Acquisition setup

Close the software
16. Close the camera software
17. Stop the openSIM software by clicking the stop button (C4) and close the software
→ Important to stop execution by stop button on front panel and not by ‘Abort Execution’ button in the LabView toolbar

Note: Repertoire

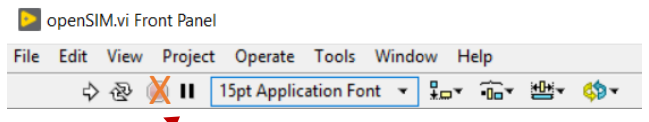
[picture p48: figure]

Repertoires (.repz file) have to be loaded only once to the SLM
→ Selecting repertoire path (C20) and sending repertoire path (C21) should be performed only when using the software for the first time after assembling the openSIM or if the user wants to load additional repertoires to the SLM

## 7. Data handling

- The base data directory is the folder ‘openSIMdata’ in the same directory than the openSIM application (when running the openSIM software for the first time this folder is generated)
- Folder for imaging session: When clicking C12 (to save the parameter) for the first time after starting the application a folder for all the data generated during this imaging session (defined by start and stop of the application) is automatically created with the current date as file name (‘imaging_date’)
- Folder for individual image acquisition: Within the imaging session folder, a folder with the data of each SIM image acquisition is generated with C11 and an incrementing number (e.g. ‘1_SIM_data’, ‘2_SIM_data’, …) as file name, such a folder is generated each time C12 is clicked (having a folder for each SIM image acquisition with corresponding metadata and used pattern sequence ensures the automatic and correct linkage between data and metadata needed for the image reconstruction and facilitates the read in of the data with corresponding metadata with the SIMToolbox)
- → clicking C12 should correspond to one SIM image acquisition with the camera software (i.e. C12 should be clicked before each SIM image acquisition execution with the
camera software)
→ within this folder the corresponding txt with the metadata and the used pattern sequence are saved besides the imaging data
→ this folder should be selected as directory for the imaging data in the camera software
- The acquired images should be saved in tiff format (camera software acquisition settings)
- The tiff format is a commonly used file format (lossless file format) compatible with ImageJ and the image reconstruction software SIMToolbox (MATLAB toolbox for structured illumination fluorescence microscopy)

Do not stop the program here!

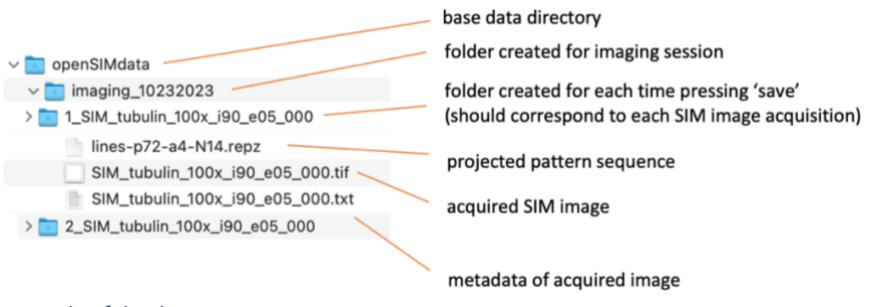
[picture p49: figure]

Example of the data structure

## 8. Troubleshooting

Problem | Possible reason | Possible Solution
When first running the openSIM application, it is not possible to connect to the SLM | The openSIM application might encounter problems connecting to the SLM due to missing drivers | Download the openSIM application file from here (https://zenodo.org/records/10067217) and extract it on your local drive. Try to run the openSIM software from this file.
It is not possible to connect to the NI DAQ and/or SLM → error message(s), I2 does not light green and software automatically stops execution) → if the openSIM software cannot establish the communication with the SLM and/or DAQ an automatic error message will appear and the software execution is stopped | The openSIM software was closed by clicking the ‘Abort execution’ at the Labview toolbar instead of clicking the stop bottom (C4). By clicking the user interface stop bottom it is assured that the NI DAQ and SLM are set back to their default settings and that the devices are closed properly. Not doing so can lead to reconnection problems when subsequently restarting the software. | Close the openSIM LabView application and camera software and reopen them. If this does not solve the problem close the applications and dis- and reconnect the USB connection between the individual devices (SLM, DAQ) and PC. Then start the applications again. If it is still not possible to connect to the devices, close the applications and restart the computer.

When executing the
openSIM application for the first time, it is not possible to connect to the DAQ
despite the device being
connected

The NI DAQmx software
driver is not installed

The NI DAQmx version is
older than the LabView
runtime engine version

Download (https://www.ni.com/en/support/downloads/software-products/download.package-manager.html#322516) the free NI package manager and check if the driver is installed

Check in the NI package manager if the NI DAQmx version 18.1 (or newer) is installed

In order to check if the NI DAQ USB 6001 is detected by the PC, the ‘Windows Device Manager’ or ‘NI Measurement & Automation

| | Explorer – NI max’ (free software which provides access to NI hardware; information how to download NI Max can be found here). (https://knowledge.ni.com/KnowledgeArticleDetails?id=kA03q000000YGQwCAO&l=en-CH) NI max can also be used to troubleshoot the DAQ control independent of the openSIM software via If the NI DAQ does not appear in the NI DAQmx, you can find further support here. (https://knowledge.ni.com/KnowledgeArticleDetails?id=kA00Z000000P7OaSAK&l=en-CH)
When executing the openSIM application for the first time, it is not possible to connect to the SLM | Another version than Microsoft Visual Studio 2013 is installed. | You may encounter compatibility issues if you attempt to run the openSIM software with a different version of Visual Studio. You can find the Visual Studio Express 2013 download (https://visualstudio.microsoft.com/vs/older-downloads/) here. A license/key is not needed for the Express version. If this does not solve the problem, try to connect to the SLM via the MetroCon software itself. There one can test connecting to the SLM and uploading a repertoire independent of the openSIM software.
It is not possible to load a repertoire to the SLM | The directory of the .bat file is not correct (see section 3), or the bat file is missing. | The repertoire can alternatively be selected and uploaded to the SLM via the MetroCon software instead of using the openSIM software.
When enabling z-stacking error message appears | Z-actuator at peripheral component selection is not enabled (C6) | Enable z-actuator and try to enable z-stacking again

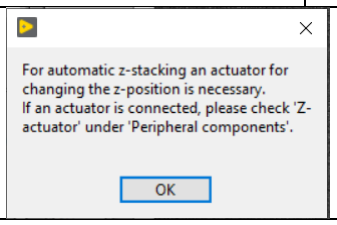
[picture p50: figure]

## Appendix

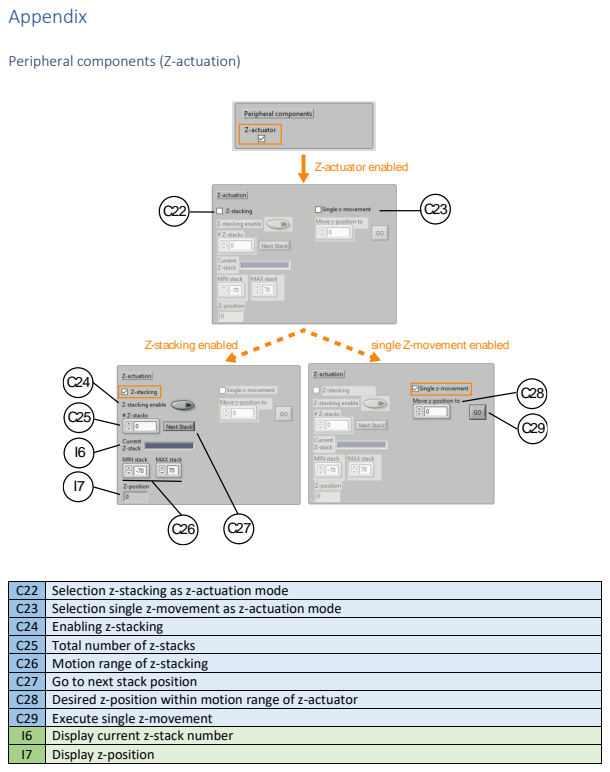
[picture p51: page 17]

C22 | Selection z-stacking as z-actuation mode
C23 | Selection single z-movement as z-actuation mode
C24 | Enabling z-stacking
C25 | Total number of z-stacks
C26 | Motion range of z-stacking
C27 | Go to next stack position
C28 | Desired z-position within motion range of z-actuator
C29 | Execute single z-movement
I6 | Display current z-stack number
I7 | Display z-position

An external objective positioning system can be used to precisely adjust the z-position of the objective. In the openSIM software we implemented options to control a z-actuation device in order to automatically move the objective to a certain position (‘single z-movement’) or automatically subsequentially move the z-position of the objective to specified positions in order to acquire a z-stack of the sample (‘Z-stacking’). We used the piezo actuation system MIPOS 100 (Piezosystem Jena) as z-actuator. The implemented z-stacking/single z-movement uses an analog signal via the DAQ device to control the piezo focus positioner. The piezo focus lens positioner can move objectives in a precise and accurate way. To do so, the piezo positioner is attached to the standard optical microscope. The objective is then screwed into the piezo positioner instead of the objective turret. The currently implemented motion range limits are based on the MIPOS 100 system. Please see schematic below on how to mount the MIPOS 100 actuator.

→ When ‘Z-actuator’ (C5) is selected under ‘Peripheral components’ the parameter settings for ‘Z-stacking’ (C22) and ‘Single z-movement’ (C23) become visible but greyed out
→ Depending on the selection of ‘Z-stacking’ (C22) or ‘Single z-movement’ (C23) the corresponding settings get enabled

ADDITIONAL INDICATOR AND CONTROLS

I7: Display z-position
→ current position of z-actuator in µm during z-stacking

C22: Selection z-stacking as z-actuation mode
→ when selected corresponding settings (C24, C25, C26, C27, I6, I7) are enabled and possible to set → relative to mid-position (half of the piezo motion range), mid-position is used as initial position

C23: Selection single z-movement as z-actuation mode
→ when selected corresponding settings (C28, C29) are enabled and possible to set
→ relative to mid-position (half of the piezo motion range), mid-position is used as initial position
→ independent of z-stacking: if z-stacking is enabled, the piezo focus positioner will be set back to its initial mid-position

C24: Enabling z-stacking
→ enables the z-stacking mode
→ after inserting the necessary parameter for z-stacking (C25, C26) z-stacking should be enabled in order to subsequently execute the z-movements for the z-stack

C25: Total number of z-stacks
→ Defines the number of desired z-positions for the z-stack

C26: Motion range of z-stacking (minimum, maximum) in µm
→ defines the first (at minimum position of motion range) and last (at maximum position of motion range) position of the z-stack
- min: z-position of first stack relative to mid-position
- max: z-position of last stack relative to mid-position
→ depending on the selected number of stacks (C25) the distance between the individual stack is evenly distributed (operating principle is depicted in schematic below)
→ the selected motion range has to lie in the physical limits of the used z-actuator
→ the current limits are set to -70µm and 70µm based on the used MIPOS 100

C27: Go to next stack position
→ as the image acquisition is initiated externally with the camera software, the command for the next step has to be issued manually
→ after each acquired SIM image (via the used camera software) the next stack (subsequent z-position) has to be initiated by clicking the button (also for first stack at C26 min)

C28: Desired z-position within motion range of z-actuator
→ focus positioner moves to inserted z-position in µm relative to mid-position by clicking C29 → value has to be within motion range of piezo focus positioner, for MIPOS 100 -70µm –70µm

C29: Execute single z-movement

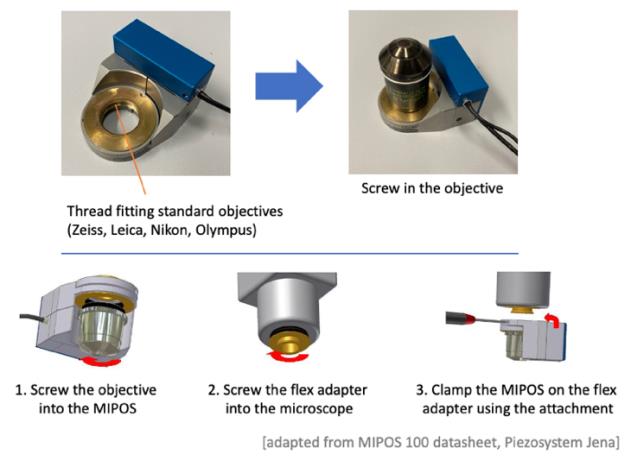
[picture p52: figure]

Images depicting how to mount MIPOS and objective


Schematic illustrating z-stacking via piezo focus positioner

Automatic pattern selection mode

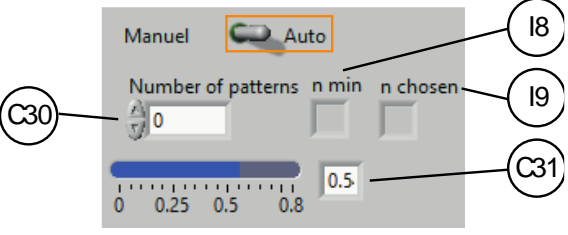
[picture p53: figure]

C30 | Desired number of patterns
C31 | Slider to select period of grading
I8 | Minimal possible period of grading
I9 | Selected period of grading

Running order (pattern sequence) selection modes
→ default: manual mode (if manual mode is selected the parameter settings necessary for automatic running order selection mode are not visible, as soon as automatic mode is selected the parameter settings become visible and enabled)
→ manual mode: the user has to select the desired running order (pattern sequence) from the available list of running orders (C14) of the currently uploaded repertoire (I5) manually, the selectable pattern sequences are defined by the repertoire uploaded to the SLM
→ auto mode: the running order (pattern sequence) is automatically selected based on the selected period (I9) and the desired number of projected patterns within the sequence (C36)

I8: Calculated minimal period
→ minimal spatial period of pattern which can be applied with the used microscope and objective → based on calculated microscope resolution, camera pixel size and magnification of objective (C7)

I9: Selected spatial period
→ running order (pattern sequence) is automatically selected from list of available running orders based on the selected spatial period
→ selected based on minimally usable spatial period (I8) and slider (C31)

C30: Desired number of patterns in the set of patterns
→ defines the number of SIM images per SIM image acquisition (I3)

C31: Slider in %
→ determines how close the period of the grating is to the minimal possible value (I8), selected value is displayed on the right (relevant for auto running order selection mode)
→ maximal 80% possible

Test pattern
- For test purposes the SLM can project static patterns. Currently four test pattern are implemented (white, black, bars1, bars2 (pattern with vertical lines))
- When test pattern (C15) is enabled, the dropdown list of available patterns becomes visible and when test pattern is disabled the list becomes greyed out
- In contrast to the sets of patterns for SIM imaging, the pattern is static and does not change
- To project the pattern the camera acquisition mode of the used camera software should be used

Status/log information

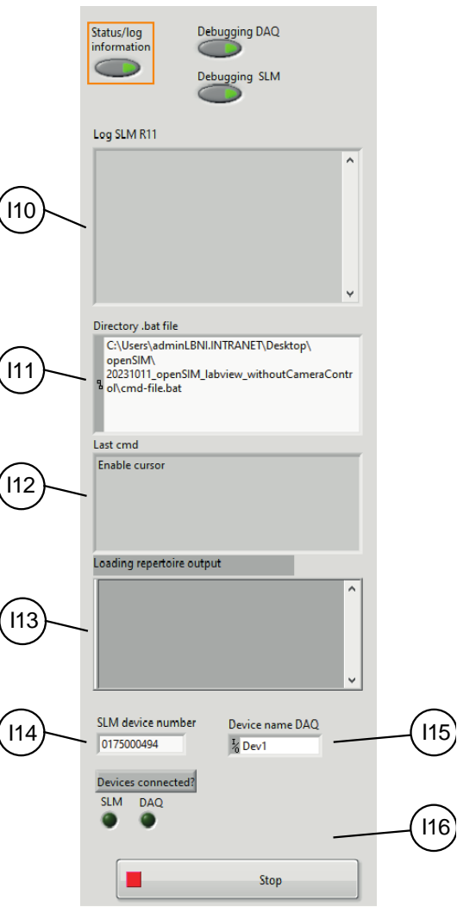
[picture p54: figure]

I13

I10 | Display current status of SLM
I11 | Directory of .bat file
I12 | Last executed command
I13 | Text which was passed to command line
I14 | Device number SLM
I15 | Device name of DAQ
I16 | Indicator if software is running

ADDITIONAL INDICATORS:

I10: Display showing the current status of the SLM R11
→ e.g. bat file cleared/loaded, repertoire loaded, load running order number, cannot load running order number, pattern send, device closed

I11: Directory of .bat file
→ the bat file (distributed with the openSIM software) contains commands for the SLM in order to load the repertoire
→ the directory of the bat file should not be changed

I12: Display showing the last executed command in the openSIM program

I13: Display showing the text which is passed to the command line in order to run a system command sent to the SLM (bat file to load repertoire)

I14: Device number of connected SLM

I14: Device name of connected data acquisition (DAQ) device
→ device name is shown when USB cable of DAQ device is connected to the PC

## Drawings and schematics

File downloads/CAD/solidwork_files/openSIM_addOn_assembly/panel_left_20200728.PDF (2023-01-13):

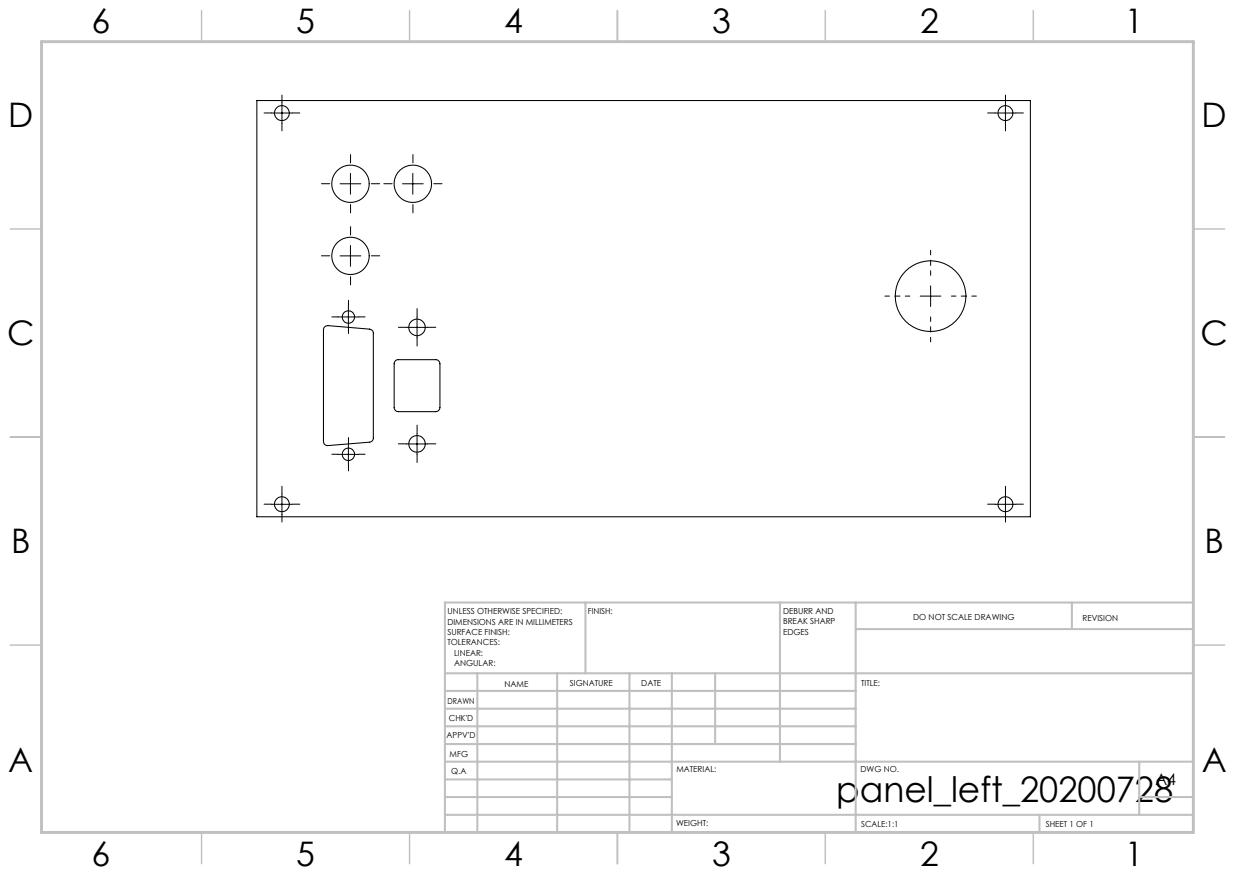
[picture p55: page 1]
FINISH:; DEBURR AND; BREAK SHARP; DO NOT SCALE DRAWING; REVISION; SCALE:1:1; SHEET 1 OF 1

UNLESS OTHERWISE SPECIFIED:
DIMENSIONS ARE IN MILLIMETERS
SURFACE FINISH:
TOLERANCES:
LINEAR:
ANGULAR:

NAME | SIGNATURE | DATE | | | | TITLE:

DRAWN
CHK'D
APPV'D
MFG
Q.A | | | | MATERIAL: panel_left_20200728 | DWG NO. | A4

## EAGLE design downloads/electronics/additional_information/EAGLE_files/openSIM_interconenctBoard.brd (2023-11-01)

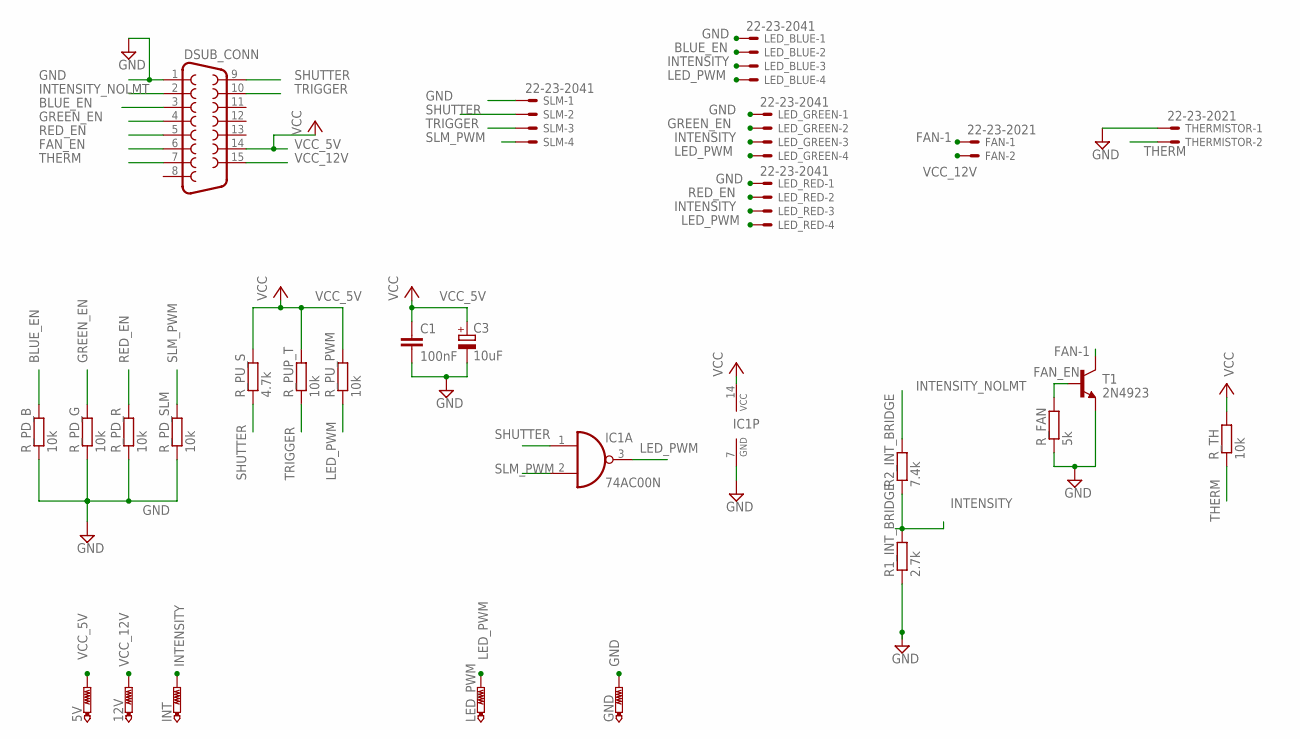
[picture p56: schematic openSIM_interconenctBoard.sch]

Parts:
5V, 12V: PTR1PAD1-20; P1-20
C1: 100nF; C050-025X075
C3: 10uF; E2,5-6E
DSUB_CONN: F15V
FAN: 22-23-2021
GND: PTR1PAD1-13Y; P1-13Y
IC1: 74AC00N; DIL14
INT: PTR1PAD1-20; P1-20
LED_BLUE: 22-23-2041
LED_GREEN: 22-23-2041
LED_PWM: PTR1PAD1-20; P1-20
LED_RED: 22-23-2041
R1_INT_BRIDGE: 2.7k; 0207/10
R2_INT_BRIDGE: 7.4k; 0207/10
R_FAN: 5k; 0207/10
R_PD_B: 10k; 0207/10
R_PD_G: 10k; 0207/10
R_PD_R: 10k; 0207/10
R_PD_SLM: 10k; 0207/10
R_PUP_T: 10k; 0207/10
R_PU_PWM: 10k; 0207/10
R_PU_S: 4.7k; 0207/10
R_TH: 10k; 0207/10
SLM: 22-23-2041
T1: 2N4923; TO126
THERMISTOR: 22-23-2021

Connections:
BLUE_EN: DSUB_CONN.3, LED_BLUE.2, R_PD_B.2
FAN-1: FAN.1, T1.2 (C)
FAN_EN: DSUB_CONN.6, R_FAN.2, T1.3 (B)
GND: C1.2, C3.-, DSUB_CONN.1, GND.TP, IC1.7 (GND), LED_BLUE.1, LED_GREEN.1, LED_RED.1, R1_INT_BRIDGE.1, R_FAN.1, R_PD_B.1, R_PD_G.1, R_PD_R.1, R_PD_SLM.1, SLM.1, T1.1 (E), THERMISTOR.1
GREEN_EN: DSUB_CONN.4, LED_GREEN.2, R_PD_G.2
INTENSITY: INT.TP, LED_BLUE.3, LED_GREEN.3, LED_RED.3, R1_INT_BRIDGE.2, R2_INT_BRIDGE.1
INTENSITY_NOLMT: DSUB_CONN.2, R2_INT_BRIDGE.2
LED_PWM: IC1.3 (O), LED_BLUE.4, LED_GREEN.4, LED_PWM.TP, LED_RED.4, R_PU_PWM.1
RED_EN: DSUB_CONN.5, LED_RED.2, R_PD_R.2
SHUTTER: DSUB_CONN.9, IC1.1 (I0), R_PU_S.1, SLM.2
SLM_PWM: IC1.2 (I1), R_PD_SLM.2, SLM.4
THERM: DSUB_CONN.7, R_TH.1, THERMISTOR.2
TRIGGER: DSUB_CONN.10, R_PUP_T.1, SLM.3
VCC_5V: 5V.TP, C1.1, C3.+, DSUB_CONN.14, IC1.14 (VCC), R_PUP_T.2, R_PU_PWM.2, R_PU_S.2, R_TH.2
VCC_12V: 12V.TP, DSUB_CONN.15, FAN.2

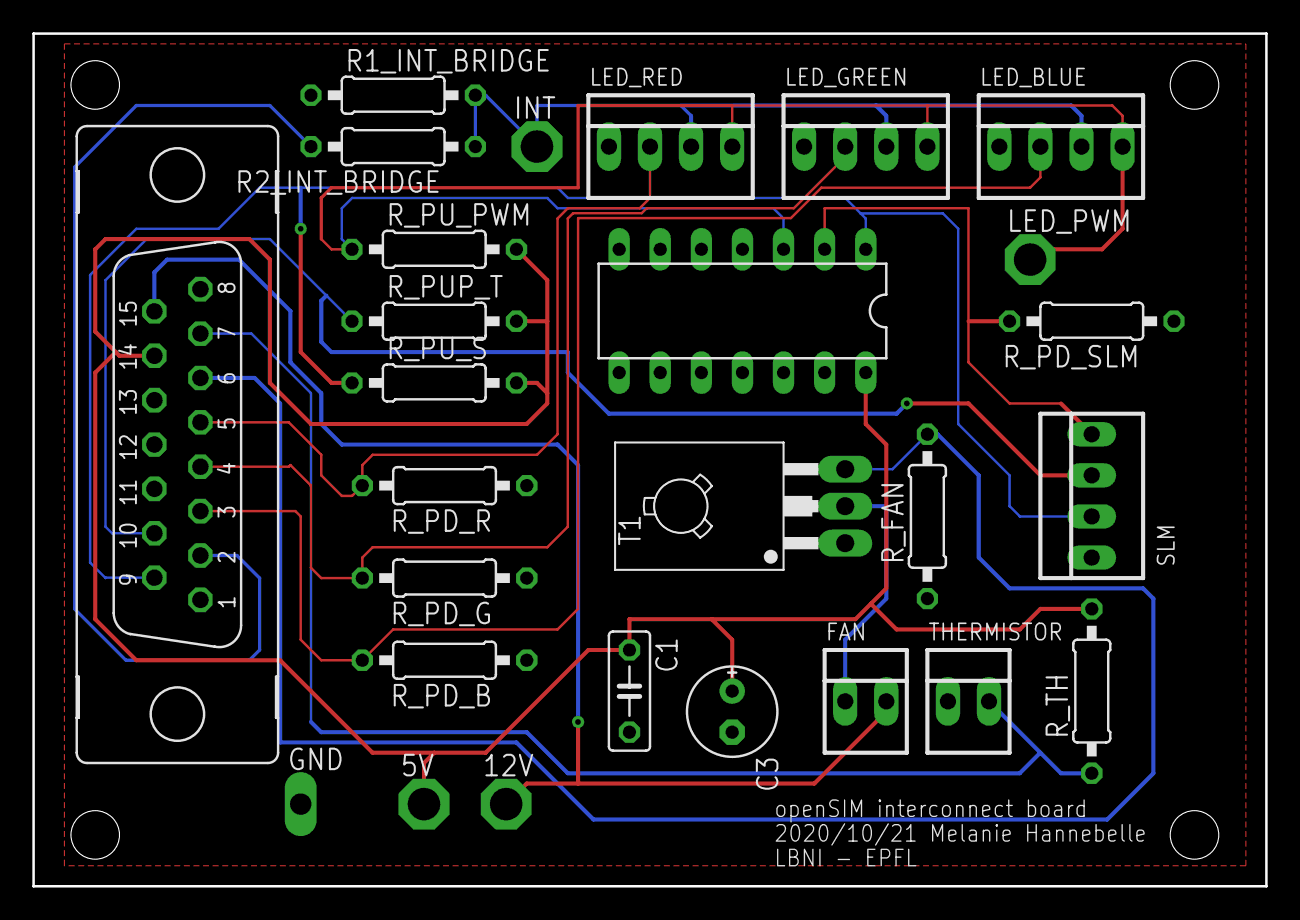
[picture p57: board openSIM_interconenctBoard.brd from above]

Board: 2 copper layers, 76.2 x 52.7 mm, 27 parts (0 on the bottom side), 15 nets.
